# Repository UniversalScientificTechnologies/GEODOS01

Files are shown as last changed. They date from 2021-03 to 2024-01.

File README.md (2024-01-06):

# GEODOS01B - Stand-alone ionizing radiation monitor

*Open-source scintillation detector of ionizing radiation. The device can be further modified according to specific requirements. The character of its construction makes it especially suitable for placement into mountains for in-field measurements*

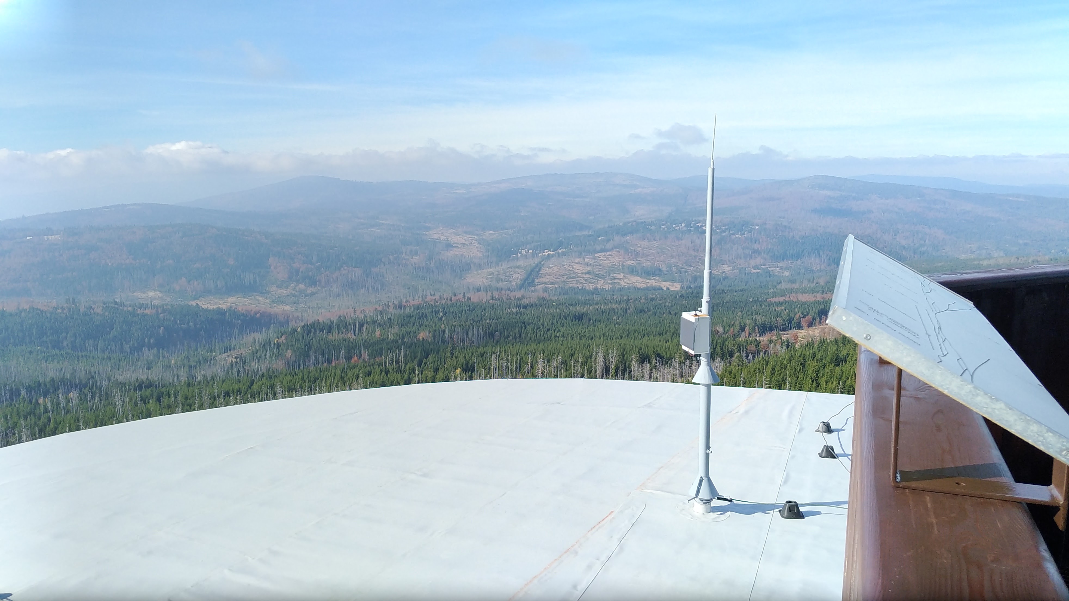
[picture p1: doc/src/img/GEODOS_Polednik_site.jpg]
GEODOS01A Installed on Polednik site


If you need a fully automatic ionizing radiation dosimeter-spectrometer device (with internal logging and a backup power supply) or a device designed for outdoor use without the possibility of connecting to a power supply and data network [GEODOS01](https://github.com/UniversalScientificTechnologies/GEODOS01) might be a better option. We can help you in choosing the most suitable device or even design and develop a new one according to your requirements. In either case, reach us using email [support@ust.cz](mailto:support@ust.cz).

### Locations

GEODOS devices are mounted in multiple significant locations around Europe at this moment.

#### Chernobyl Red Forest

One GEODOS device is installed in [Chernobyl Red Forest site](https://en.wikipedia.org/wiki/Red_Forest).

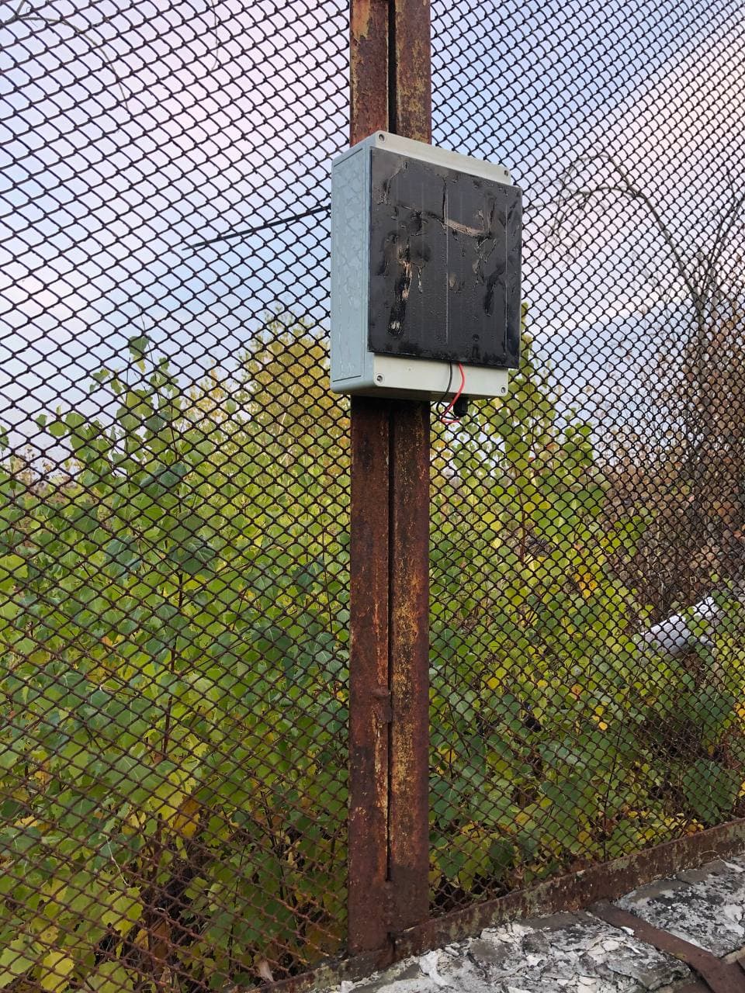
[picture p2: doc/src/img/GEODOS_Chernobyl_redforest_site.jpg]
GEODOS01A Installed in Chernobyl Red Forest site


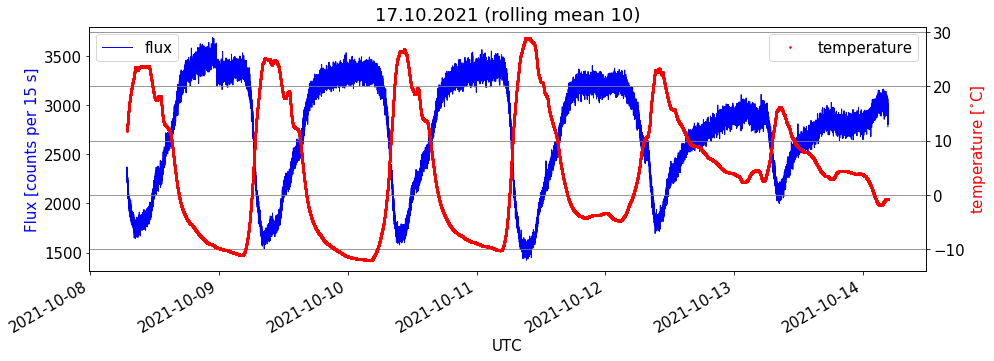
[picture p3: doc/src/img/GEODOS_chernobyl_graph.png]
GEODOS01A raw data before temperature compensation


#### Šumava mountains

GEODOS devices are installed in multiple locations in Šumava. For example example at [Polednik watch tower](https://cs.wikipedia.org/wiki/Poledn%C3%ADk_(%C5%A0umava)).

GEODOS01A Installed on Polednik site

#### Kosetice Atmospheric Tower

The [National Atmospheric Observatory Košetice](https://actris-ri.cz/) (NAOK) was established by the Czech Hydrometeorological Institute as a department specialized in long-term air quality monitoring and research at the background scale in 1988. The GEODOS is located here by [CRREAT project](http://www.ujf.cas.cz/en/research-development/large-research-infrastructures-and-centres/crreat/objectives/).

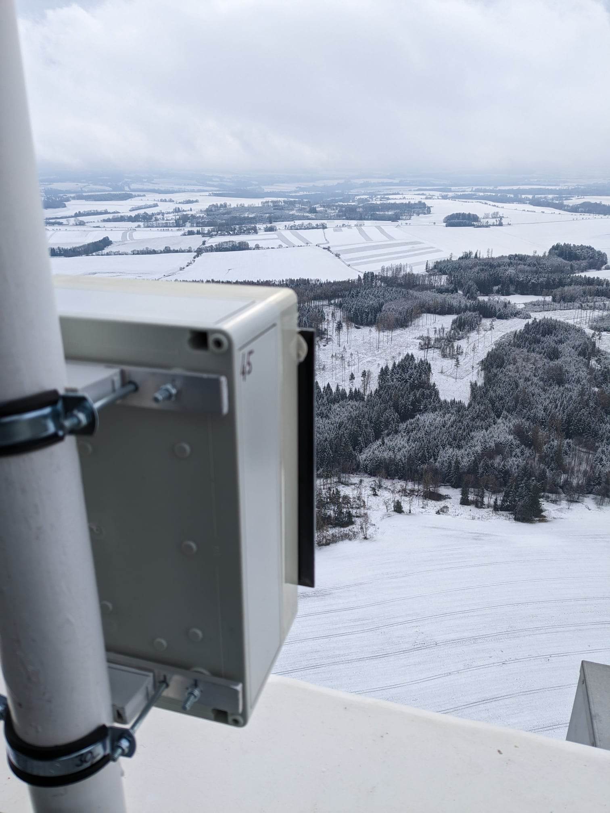
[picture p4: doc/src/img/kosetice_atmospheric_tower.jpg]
GEODOS01B Installed Kosetice Atmospheric Tower


### Technical parameters

* Detection element: scintillation crystal NaI(Tl) 14 mm in diameter, 20 mm in length, integrated with SiPM detector
* Power source: solar panel
* Backup power source: [LTO cells](https://en.wikipedia.org/wiki/Lithium-titanate_battery)
* Data memory: SD card
* Record’s content: energy and time of each event above the specified energy (1MeV by default)
* Record’s periodicity: 10 s (maximal dead time 2 s)
* Time resolution: 20 us
* ADC Conversion time: 104 us
* [Dead time](https://en.wikipedia.org/wiki/Dead_time): 2 us
* Accuracy of event’s time: 500 ns
* Energy range: 0.3 to 18 MeV (deposited energy)
* Spectral Resolution: 0.02 MeV
* Open-source HW and SW
* Device status indicator type: LED
* Uninterrupted measurement campaign interval: 6 months for 2 GB SD card
* LoRa connection to IoT network
* Charging temperature range: -20°C to +35°C
* Operational temperature range: -30°C to +50°C
* Dimensions 254x180x111 mm [enclosure TK PS 2518-11-o](https://www.spelsberg.co.uk/industrial-housing/with-/-without-metric-knock-outs/11090801/)
* Weather protection [IP 33](https://en.wikipedia.org/wiki/IP_code)

### Device block diagram

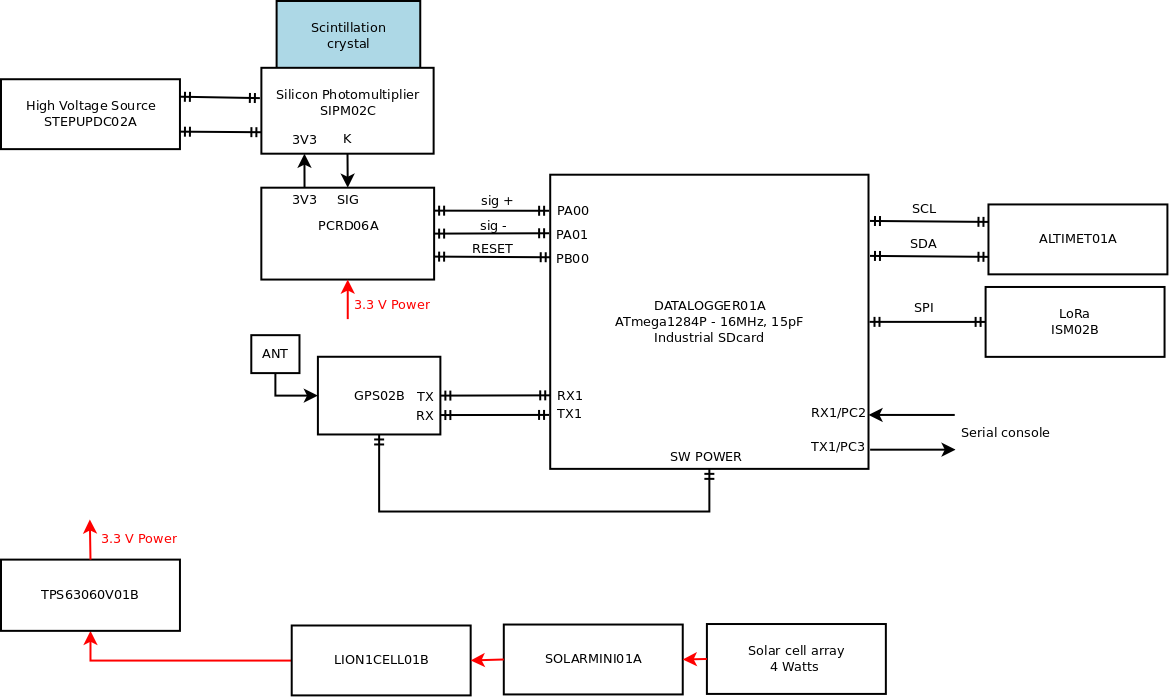
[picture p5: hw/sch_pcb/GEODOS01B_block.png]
GEODOS01A block diagram


### Sensor element

The core of the detector is a scintillation crystal with [SiPM detector](https://en.wikipedia.org/wiki/Silicon_photomultiplier).

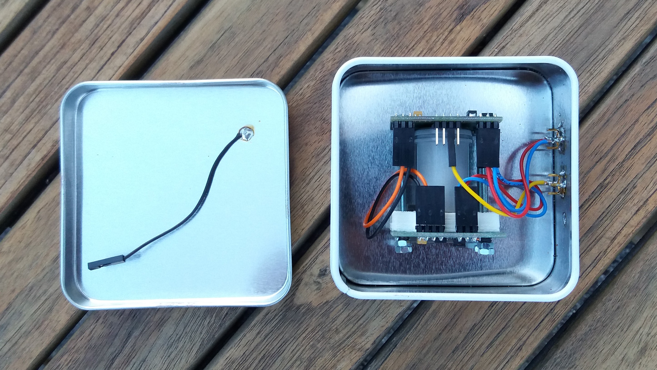
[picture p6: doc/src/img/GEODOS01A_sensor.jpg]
Scintillation detector in box


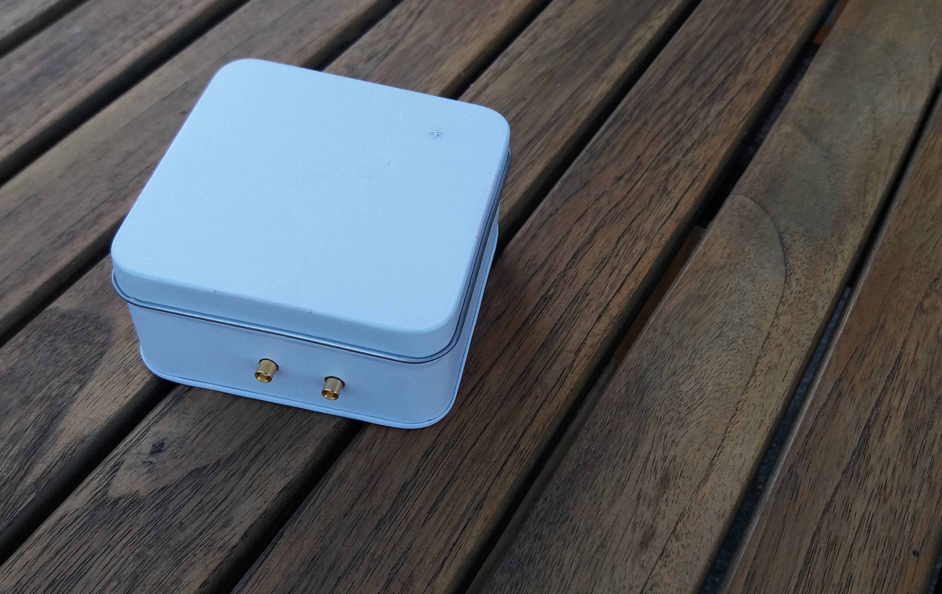
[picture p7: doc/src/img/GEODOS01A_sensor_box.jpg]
Scintillation detector housing


### Data storage

The primary raw data is stored in the SD card's memory. The IoT network is used for telemetry data transfer, and device monitoring (e.g. temperature, humidity, pressure, battery voltage, etc.). We are regularly using the [TTN](https://www.thethingsnetwork.org/), but the device could be configured for use with any IoT LoRa-based network.
For remote areas, mounting an IoT gateway in the radio range of GEODOS instruments could also be a good option.

#### Messages

#### About message

As a second message, when turned on, a string is sent that uniquely identifies the device.

```
$DOS,GEODOS01B,L02,256,379276a,1290c00806a200914056a000a0000086
```
* `$DOS` - is the first character of the message string
* `GEODOS01B` - Name of the device. In this case, it is GEODOS
* `L02`- FW version
* `256` - ADC offset
* `379276a` - Hash of commit with this firmware
* `1290c00806a200914056a000a0000086` - Unique serial number of dosemeter instrument

#### Data message

The output data are in the form of textual [NMEA-0183](https://en.wikipedia.org/wiki/NMEA_0183) like strings. There are two main message types - Histogram message ($HIST) and events stream message ($HITS). Both of these messages could be combined in data output from a single device.  

##### Histogram message

```
$HIST,8,118.15,960.09,4.06,2.33,394,803,0,3,30656,2401,1304,5,3,4,7,9,5,4,6,7,4,3,0,8,2,3,1,1,1,4,3
```

* `$HIST` - Marking a message with spectrums
* `count` - Message number since restart or power-up
* `time` - Time in seconds from power-up
* `suppress` -
* `dose` - Number of detected particles
* `offset` - ADC offset. Specifies the zero channel position.
* `energetic channels` - All remaining values indicate a certain energy channel. From the smallest to the largest. The third value is 1st channel.

##### Events message

```
$HITS,20,916,84,2984,37,16386,38,30666,26,38530,48,43043,27,49257,100,53904,43,59650,32,65631,32,65802,46,68555,47,71124,53,73601,48,74179,59,77454,72,90563,30,98074,74,98901,124,99743,50
```
* `$HITS` - Marking a message with individual events
* `hit count` - Number of events captured from the last HITS message
* `time` - Time in seconds from power-up
* `hit channel` - Channel corresponding to the captured event

### Detailed documentation of the used electronic modules

* [STEPUPDC02A](https://github.com/mlab-modules/STEPUPDC02)
* [SIPM02C](https://github.com/mlab-modules/SIPM02) known as "AIRDOSC01A_PCB01C"
* [PCRD06A](https://github.com/mlab-modules/PCRD06)
* [GPS01B](https://www.mlab.cz/module/GPS01B)
* [DATALOGGER01A](http://mlab.cz/module/DATALOGGER01A)
* [ALTIMET01A](https://github.com/mlab-modules/ALTIMET01)
* [ISM02B](https://github.com/mlab-modules/ISM02)
* [TPS63060V01A](https://github.com/mlab-modules/TPS63060V01)
* [LION1CELL01B](https://github.com/mlab-modules/LION1CELL01)
* [SOLARMINIBAT01A](https://github.com/mlab-modules/SOLARMINIBAT01)
* [SOLARMINI01B](https://github.com/mlab-modules/SOLARMINI01)

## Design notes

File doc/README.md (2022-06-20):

# Advanced user documentation of GEODOS

# Uvedení do provozu

Při instalaci zařízení musí být splněno:

  * Přívod energie - buď fotovoltaickým panelem, nebo napájením z jiného 5V zdroje
  * GPS anténa musí být umístěna tak, aby měla výhled na oblohu (Nalepena na vrchní stranu krabice, do volného okna v observatoři nebo podobně)
  * Do zařízení musí být vložena zformátovaná SDkarta na kterou se budou zapisovat data.  

## Zapnutí přístroje

Po splnění těchto podmínek je možné zařízení zapnout vypínačem. Směrem k LED je zapnuto.

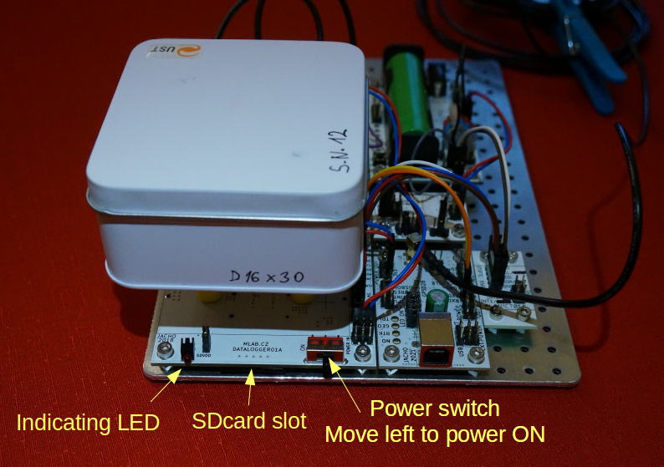
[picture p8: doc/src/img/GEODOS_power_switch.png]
GEODOS01 power switch


Po zapnutí se spustí GPS, což je indikováno LED na modulu GPS02B do kterého vede GPS anténa. Následně zařízení přibližně minutu čeká na získání fixu pozice. Získání fixu je indikováno blikáním zelené LED na modulu GPS02B.
Následně každých 10sekund blikne červená LED na levo od vypínače, což indikuje zápis na SDkartu.

## Získávání dat

GEODOS dovede data na SDkartu zaznamenávat velmi dlouho. Šest měsíců záznamu odpovídá přibližně 500MB dat. Běžné velikosti SDkaret umožňují kontinuální záznam řádově v rocích provozu. Z tohoto důvodu je GEODOS vybaven LoRa telemetrií, aby bylo možno přibližně monitorovat jeho funkčnost.  
Používat GEODOS tímto způsobem ale není úplně rozumné, neboť tato vzdálená telemetrie není schopna monitorovat kvalitu dat. Je tak dobré data manuálně stahovat buď pravidelně, nebo na základě výskytu významných událostí.

## Vypnutí přístroje a vyčtení dat

Díky způsobu fungování, kdy přístroj zaznamenává na SDkartu jednou za 10 sekund je vhodné vypnutí provést tak, že **počkáme na dvojbliknutí červené LED vlevo od vypínače a následně vypínačem vypneme napájení**.
Tento postup minimalizuje možnost poškození souborového systému na SDkartě nedokončeným zápisem.

Následně je možná SDkartu vyjmout zatáhnutím nehtem (SDkarta je umístěna v prostoru mezi vypínačem a indikační LED).

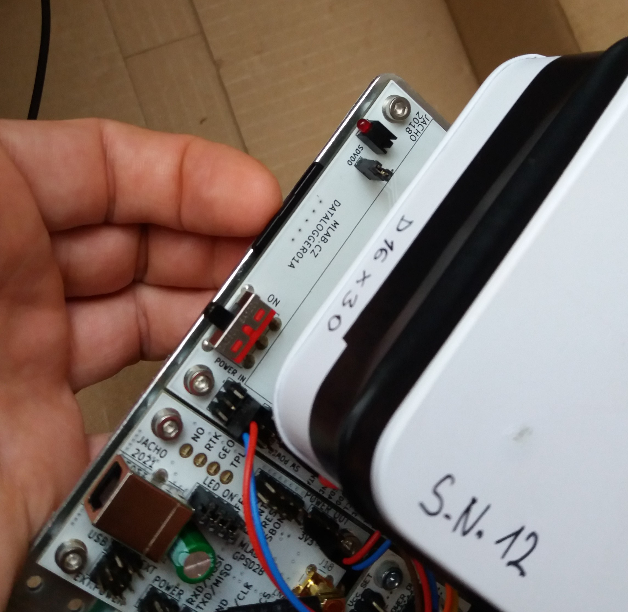
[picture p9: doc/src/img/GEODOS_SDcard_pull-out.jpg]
SDcard removing


SDkartu lze přečíst v běžné čtečce SDkaret. Vyzkoušeným typem je například [Kingston USB 3.0 High-Speed Card Reader](https://www.kingston.com/us/memory-card-readers/usb-3-0-high-speed-media-reader)

Na SDkartě je pak za normílních okolností pouze jeden soubor DATALOG.TXT, který obsahuje všechny zaznamenané informace.  

## Service information

### Debug output

GEODOS has debug output at RX0, TX0 baudrate is 38400.

  $HIST,63,861.90,97386.50,25.81,3.82,16,473,883,2,12704,21600,80,16,11,0,3,5,1,1,3,0,1,2,1,1,1,0,0,1,0,0,0,2
  $HITS,29,4879,35,5201,30,17202,36,18704,30,21061,102,27156,61,27574,79,27797,26,32746,40,40409,58,48144,36,49356,54,51772,37,52090,69,56941,61,62446,36,63116,132,65634,104,67413,35,68563,32,70039,30,70211,56,83196,28,83445,63,87672,32,88476,29,92791,26,99154,84,99543,29

### Firmware upgrade

For the firmware upgrade, the USB-RS232 converter is needed.  Normally is used the [USB232R02](https://github.com/mlab-modules/USB232R02), but any [USBcable](https://techfun.sk/produkt/kabel-pl2303hx-usb-na-ttl-rs232/) could be used.

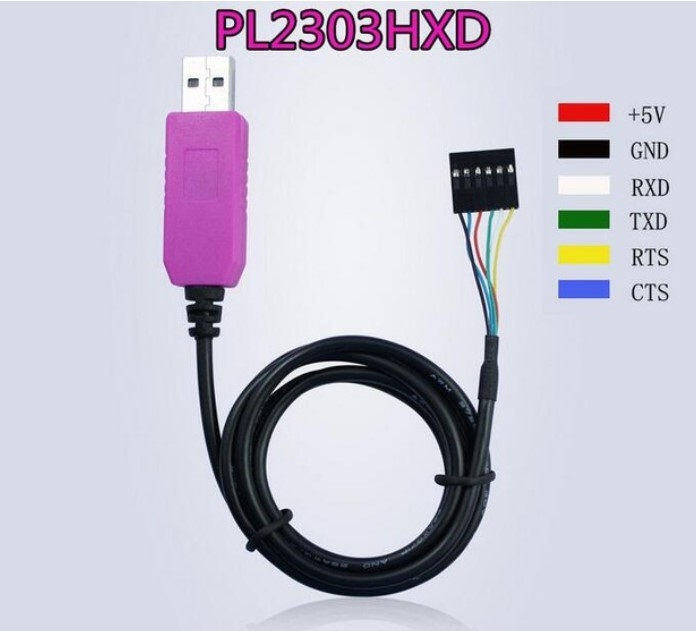
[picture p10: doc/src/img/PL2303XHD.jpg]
PL2303XHD cable


#### Cable connection

|USB converter cable | DATALOGGER01A |
|--------------|---------------|
|RX | TX0|
|TX | RX0|
|RTS | RST# |
|GND | GND|

Physical realization

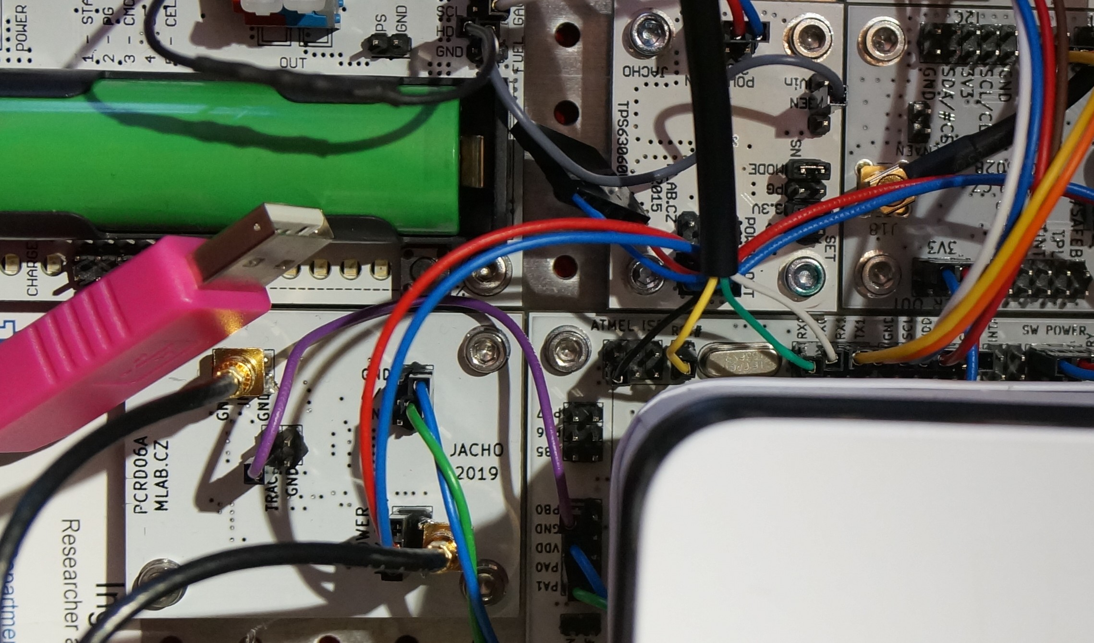
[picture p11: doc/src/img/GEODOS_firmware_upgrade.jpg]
PL2303XHD cable - DATALOGGER01A connection


#### Upgrade process

    cd fw/bin/FIRMWARE_VERSION
    ./program.sh

Expected output:

    $ ./program.sh

    avrdude: Version 6.3-20190619
             Copyright (c) 2000-2005 Brian Dean, http://www.bdmicro.com/
             Copyright (c) 2007-2014 Joerg Wunsch

             System wide configuration file is "./avrdude.conf"
             User configuration file is "/home/kaklik/.avrduderc"
             User configuration file does not exist or is not a regular file, skipping

             Using Port                    : /dev/ttyUSB0
             Using Programmer              : arduino
             Overriding Baud Rate          : 115200
             AVR Part                      : ATmega1284P
             Chip Erase delay              : 55000 us
             PAGEL                         : PD7
             BS2                           : PA0
             RESET disposition             : dedicated
             RETRY pulse                   : SCK
             serial program mode           : yes
             parallel program mode         : yes
             Timeout                       : 200
             StabDelay                     : 100
             CmdexeDelay                   : 25
             SyncLoops                     : 32
             ByteDelay                     : 0
             PollIndex                     : 3
             PollValue                     : 0x53
             Memory Detail                 :

                                      Block Poll               Page                           Polled
               Memory Type Mode Delay Size  Indx Paged  Size   Size #Pages MinW  MaxW       ReadBack
               ----------- ---- ----- ----- ---- ------ ------ ---- ------ ----- ----- --------    -
               eeprom        65    10   128    0 no       4096    8      0  9000  9000 0xff     0xff
               flash         65    10   256    0 yes    131072  256    512  4500  4500 0xff     0xff
               lock           0     0     0    0 no          1    0      0  9000  9000 0x00     0x00
               lfuse          0     0     0    0 no          1    0      0  9000  9000 0x00     0x00
               hfuse          0     0     0    0 no          1    0      0  9000  9000 0x00     0x00
               efuse          0     0     0    0 no          1    0      0  9000  9000 0x00     0x00
               signature      0     0     0    0 no          3    0      0     0     0 0x00     0x00
               calibration    0     0     0    0 no          1    0      0     0     0 0x00     0x00

             Programmer Type : Arduino
             Description     : Arduino
             Hardware Version: 3
             Firmware Version: 8.0
             Vtarget         : 0.3 V
             Varef           : 0.3 V
             Oscillator      : 28.800 kHz
             SCK period      : 3.3 us

    avrdude: AVR device initialized and ready to accept instructions

    Reading | ################################################## | 100% 0.00s

    avrdude: Device signature = 0x1e9705 (probably m1284p)
    avrdude: safemode: lfuse reads as 0
    avrdude: safemode: hfuse reads as 0
    avrdude: safemode: efuse reads as 0
    avrdude: reading input file "./AIRDOSC_1024_LS.ino.hex"
    avrdude: writing flash (25132 bytes):

    Writing | ################################################## | 100% 3.28s

    avrdude: 25132 bytes of flash written
    avrdude: verifying flash memory against ./AIRDOSC_1024_LS.ino.hex:
    avrdude: load data flash data from input file ./AIRDOSC_1024_LS.ino.hex:
    avrdude: input file ./AIRDOSC_1024_LS.ino.hex contains 25132 bytes
    avrdude: reading on-chip flash data:

    Reading | ################################################## | 100% 2.28s

    avrdude: verifying ...
    avrdude: 25132 bytes of flash verified

    avrdude: safemode: lfuse reads as 0
    avrdude: safemode: hfuse reads as 0
    avrdude: safemode: efuse reads as 0
    avrdude: safemode: Fuses OK (E:00, H:00, L:00)

    avrdude done.  Thank you.

The new firmware version should be marked at beginnig of  DATALOG.TXT file after the power-up and logging some data. e.g.

    $AIRDOS,C_LS_1024_v2,...

### Scintillation detector

Scintilační krystaly použité v GEODOSech mají různé rozměry. Rozměr krystalů je napsán na boku bílé kovové krabičky ve které je krystal umístěn.

**Při otevření krabičky je nutné mít vypnuté napájení křemíkového fotonásobiče** Při zapnutém napájení teče na světle skrz SiPM příliš velký proud a fotonásobič se zničí přehřátím.

### Photovoltaic power source

#### Solar cell array parameters

##### Elektrical parameters

- Isc = 2,3 A
- Voc= 2,5 V
- Impp= 2,1 A
- Vmpp= 2,1 V
- Pm= 4,4 Wp

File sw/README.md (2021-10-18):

# Supporting software

`lorasave.py` is a script for general logging of LoRa uplink messages to a file. It works with the The Things Network infrastructure.

It creates log files with newline-separated JSON messages. To process the logged messages and extract specific fields, you may for example use the `jq` tool, like this:

	$ cat __path_to_logs__ | jq -r '[.received_at, .end_device_ids.device_id, .device_id, .uplink_message.decoded_payload.V] | @tsv'

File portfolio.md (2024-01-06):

---
title: "Ground based radiation monitor"
name: "AAA"
excerpt: "Open-source scintillation detector of ionizing radiation. The device can be further modified according to specific requirements. The character of its construction makes it especially suitable for placement into mountains for in-field measurements"
header:
  image: products/GEODOS01B/doc/src/img/kosetice_atmospheric_tower.jpg
  teaser: products/GEODOS01B/doc/src/img/kosetice_atmospheric_tower.jpg
  overlay_color: "#000"
  overlay_filter: "0.5"
  overlay_image: products/GEODOS01B/doc/src/img/GEODOS_Polednik_site.jpg

---

GEODOS01A Installed on Polednik site

If you need a fully automatic ionizing radiation dosimeter-spectrometer device (with internal logging and a backup power supply) or a device designed for outdoor use without the possibility of connecting to a power supply and data network [GEODOS01](https://github.com/UniversalScientificTechnologies/GEODOS01) might be a better option. We can help you in choosing the most suitable device or even design and develop a new one according to your requirements. In either case, reach us using email [support@ust.cz](mailto:support@ust.cz).

### Example installations

GEODOS devices are mounted in multiple significant locations around Europe at this moment.

#### Chernobyl Red Forest

One GEODOS device is installed in [Chernobyl Red Forest site](https://en.wikipedia.org/wiki/Red_Forest).

GEODOS01A Installed in Chernobyl Red Forest site

#### Šumava mountains

GEODOS devices are installed in multiple locations in Šumava. For example example at [Polednik watch tower](https://cs.wikipedia.org/wiki/Poledn%C3%ADk_(%C5%A0umava)).

GEODOS01A Installed on Polednik site

#### Kosetice Atmospheric Tower

The [National Atmospheric Observatory Košetice](https://actris-ri.cz/) (NAOK) was established by the Czech Hydrometeorological Institute as a department specialized in long-term air quality monitoring and research at the background scale in 1988. The GEODOS is located here by [CRREAT project](http://www.ujf.cas.cz/en/research-development/large-research-infrastructures-and-centres/crreat/objectives/).

GEODOS01B Installed Kosetice Atmospheric Tower

### Data storage

The primary raw data is stored in the SD card's memory. The IoT network is used for telemetry data transfer, and device monitoring (e.g. temperature, humidity, pressure, battery voltage, etc.). We are regularly using the [TTN](https://www.thethingsnetwork.org/), but the device could be configured for use with any IoT LoRa-based network.
For remote areas, mounting a private IoT gateway in the radio range of GEODOS instruments could also be an option.

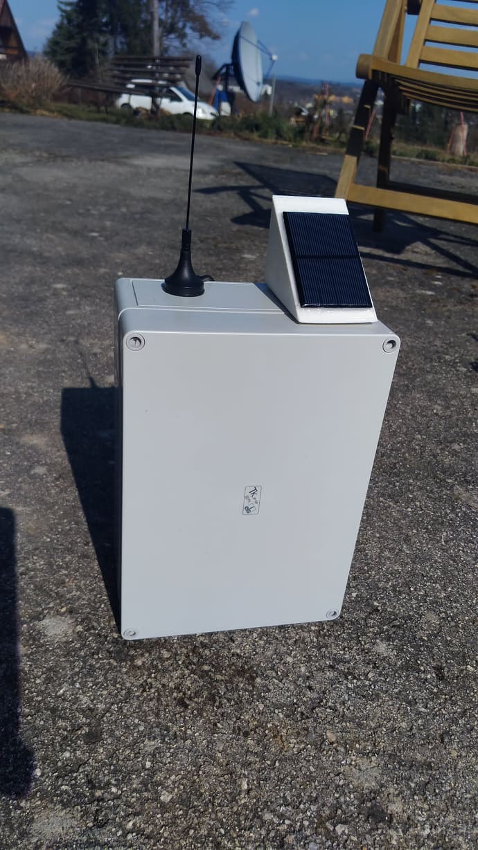
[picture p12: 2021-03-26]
doc/src/img/GEODOS01A.jpg

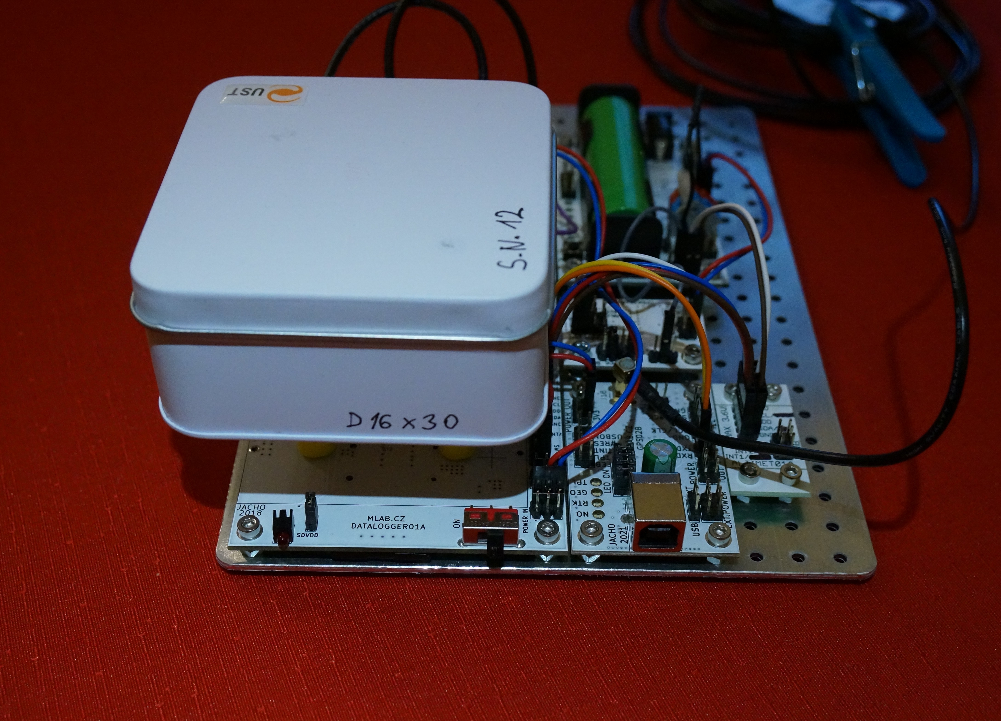
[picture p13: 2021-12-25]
doc/src/img/GEODOS_power_switch.jpg

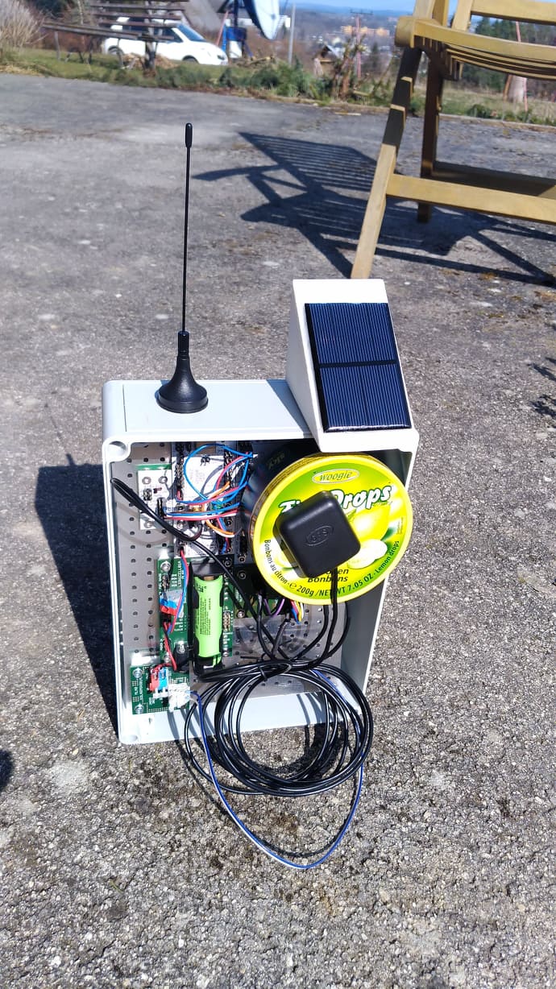
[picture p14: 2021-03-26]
doc/src/img/GEODOS01A_opened.jpg

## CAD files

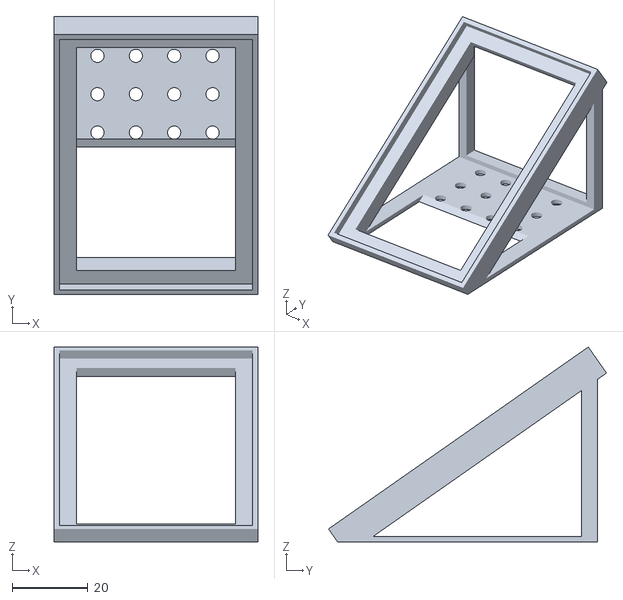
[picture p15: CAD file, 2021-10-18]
cad/stl/SolarHolder.stl
54.0 x 73.6 x 51.6

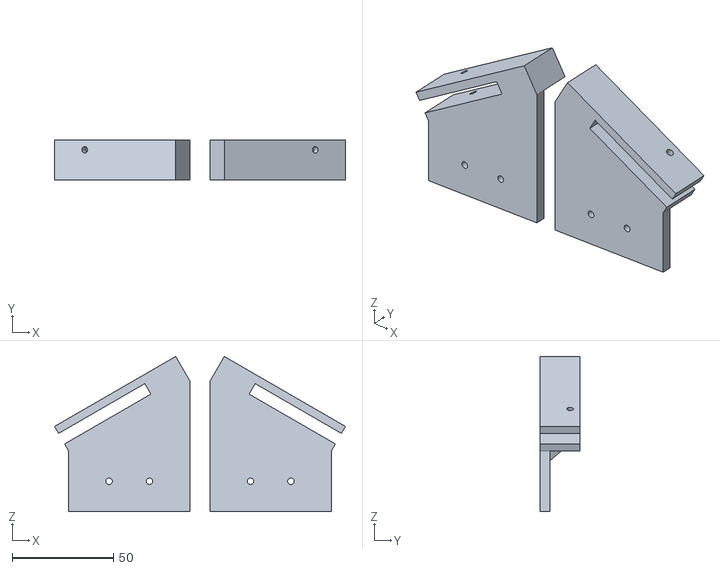
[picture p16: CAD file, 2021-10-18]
cad/stl/SolarHolder_big.stl
144.0 x 20.0 x 76.8

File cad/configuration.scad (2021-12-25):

$fn=40; // model faces resolution.

//OBECNE PARAMETRY 
//----------------------------------------------------------------
//----------------------------------------------------------------

vyska_krystalu=15;
vyska_sipm=2;
presah_krystalu=6;
rezerva_nad_krystalem=5;
vyska_drzaku_krystalu=vyska_krystalu-presah_krystalu-2;

hrana_krystalu=6; //čistá hrana

// big-big
//zakladna_krystalu_x=23.7; //1.5mm rezerva hrana SIPM je 22 mm
//zakladna_krystalu_y=23.7;
// big-small
zakladna_krystalu_x=22.0; //1.5mm rezerva hrana SIPM je 22 mm
zakladna_krystalu_y=22.0;
sila_steny=1.2;
sila_materialu_zakladny=7; //1.6;


vyska_zapusti_pro_PCB=0; //výčka krycího matriálu pro PCB a zároveň pro vytvoření vany pro zalití silikonem, kvůli světlotěsnoti.
vyska_SIPM_nad_PCB=2.4; //výška celého SIPM senzoru
tolerance_pro_dotazeni_k_SIPM=-0.5; // kvůli dotažení krystalu k SIPM
velikost_modulu_x=2; //počet der
velikost_modulu_y=4;
rotec_der_modulu=10.16;

vyska_matky=3;
sirka_matky=6.7;
prumer_sroubu=3.6;//3.4;
prumer_hlavy_sroubu=6;
vyska_hlavy_sroubu=5;

//Pro díl SIPMBOX01C_D02
D02_velikost_modulu_x=3; //počet der
D02_velikost_modulu_y=4;
D02_vyska_bocniho_prekryvu=25;

//Pro díl SIPMBOX01C_D07
D07_vyska=6;

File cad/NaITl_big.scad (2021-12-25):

include <./configuration.scad>
 
/*
difference (){
SIPMBOX01C_D05();
 
translate([-(hrana_krystalu)/2,-(hrana_krystalu)/2,0])
         
   cube([100,100,100]);   
    
}
*/

/*
difference (){
      union() {
translate([0,0,7])
          
          translate([-rotec_der_modulu/2,0,0])
          SIPMBOX01C_D01();
          
         
SIPMBOX01C_D02();

translate([-rotec_der_modulu/2,0,0])
SIPMBOX01C_D06();


SIPMBOX01C_D07();
 
 
translate([-10/2,-(D02_velikost_modulu_y+2)*rotec_der_modulu/2,sila_materialu_zakladny+vyska_krystalu+rezerva_nad_krystalem])          
SIPMBOX01C_D08();          
          

translate([-rotec_der_modulu/2,0,0])
SIPMBOX01C_D03();

translate([-(hrana_krystalu)/2,-(hrana_krystalu)/2,0])
cube([hrana_krystalu,hrana_krystalu,vyska_krystalu+vyska_sipm]);
          }
   cube([100,100,100]);       
          
          }

//*/



 SIPMBOX01C_D01();

//SIPMBOX01C_D06();

//SIPMBOX01C_D02();


 

module SIPMBOX01C_D08()
{
  vyska_sloupku=3;
   difference () 
    {
   union()       {   
    cube([10,(D02_velikost_modulu_y+2)*rotec_der_modulu,2],center=false); 
        translate([10/2,0,0]) 
        cylinder (h = 3, r= 10/2, $fn=20);
        
     translate([10/2,(D02_velikost_modulu_y+2)*rotec_der_modulu,0]) 
        cylinder (h = 3, r= 10/2, $fn=20);
    }
    
     translate([10/2,0,-0.01]) 
            cylinder (h = vyska_sloupku+1, r= (prumer_sroubu+0.2)/2, $fn=40);
    
     translate([10/2,(D02_velikost_modulu_y+2)*rotec_der_modulu,-0.01]) 
            cylinder (h = vyska_sloupku+1, r= (prumer_sroubu+0.2)/2, $fn=40);
    
    
    }
    
    
       
}





module SIPMBOX01C_D07() //drzak na ALBASE
{
  difference (){
      union() {
 //Zakladna
 translate([-((D02_velikost_modulu_x) * rotec_der_modulu+2*sila_materialu_zakladny)/2,-((D02_velikost_modulu_y+2) * rotec_der_modulu+2*sila_materialu_zakladny)/2,0])
 
 minkowski()
{
  cube([(D02_velikost_modulu_x) * rotec_der_modulu+2*sila_materialu_zakladny,(D02_velikost_modulu_y+2) * rotec_der_modulu+2*sila_materialu_zakladny,D07_vyska]);
  cylinder(r=2,h=0.1);
}







}

//otvor na cely scintilacni detektor 
translate([-(D02_velikost_modulu_x * rotec_der_modulu+2*sila_materialu_zakladny)/2+2-1,-(D02_velikost_modulu_y * rotec_der_modulu+2*sila_materialu_zakladny)/2+2-1,0])
 
 minkowski()
{
  cube([D02_velikost_modulu_x * rotec_der_modulu-2*2+2+2*sila_materialu_zakladny,D02_velikost_modulu_y * rotec_der_modulu-2*2+2+2*sila_materialu_zakladny,D07_vyska]);
  cylinder(r=2,h=0.1);
}


//otvor na sroub 1
translate([-(D02_velikost_modulu_x-1)*rotec_der_modulu/2,(D02_velikost_modulu_y+2)*rotec_der_modulu/2,-0.01]) 
    translate([0,0,-0.01]) 
        {
        cylinder (h = D07_vyska+0.12, r= (prumer_sroubu+0.2)/2, $fn=40);
    
        cylinder (h = vyska_matky, r= (sirka_matky+0.2)/2, $fn=6);
      
        }

//otvor na sroub 2
translate([(D02_velikost_modulu_x-1)*rotec_der_modulu/2,(D02_velikost_modulu_y+2)*rotec_der_modulu/2,-0.01]) 
    translate([0,0,-0.01]) 
        {
        cylinder (h = D07_vyska+0.12, r= (prumer_sroubu+0.2)/2, $fn=40);
    
        cylinder (h = vyska_matky, r= (sirka_matky+0.2)/2, $fn=6);
      
        }

//otvor na sroub 3
translate([-(D02_velikost_modulu_x-1)*rotec_der_modulu/2,-(D02_velikost_modulu_y+2)*rotec_der_modulu/2,-0.01]) 
    translate([0,0,-0.01]) 
        {
        cylinder (h = D07_vyska+0.12, r= (prumer_sroubu+0.2)/2, $fn=40);
    
        cylinder (h = vyska_matky, r= (sirka_matky+0.2)/2, $fn=6);
      
        }

//otvor na sroub 4
translate([(D02_velikost_modulu_x-1)*rotec_der_modulu/2,-(D02_velikost_modulu_y+2)*rotec_der_modulu/2,-0.01]) 
    translate([0,0,-0.01]) 
        {
        cylinder (h = D07_vyska+0.12, r= (prumer_sroubu+0.2)/2, $fn=40);
    
        cylinder (h = vyska_matky, r= (sirka_matky+0.2)/2, $fn=6);
      
        }
 
//Otvor na uchytny sroub 1
translate([0,(D02_velikost_modulu_y+2)*rotec_der_modulu/2,0]) 
    translate([0,0,-0.01]) 
        {
        cylinder (h = D07_vyska+0.12, r= (prumer_sroubu+0.2)/2, $fn=40);
         cylinder (h = vyska_hlavy_sroubu, r= (prumer_hlavy_sroubu+0.2)/2, $fn=40);
                      
        }

//Otvor na uchytny sroub 2
translate([0,-(D02_velikost_modulu_y+2)*rotec_der_modulu/2,-0.01]) 
    translate([0,0,-0.01]) 
        {
        cylinder (h = D07_vyska+0.12, r= (prumer_sroubu+0.2)/2, $fn=40);
   cylinder (h = vyska_hlavy_sroubu, r= (prumer_hlavy_sroubu+0.2)/2, $fn=40);
        }      
        
 
} 
}           
         

module SIPMBOX01C_D05() //drzak krystalu
{
  difference (){
      union() {
 //Zakladna
 translate([-(velikost_modulu_x * rotec_der_modulu)/2+2+1/2,-(velikost_modulu_y * rotec_der_modulu)/2+2+1/2,0])
 
 minkowski()
{
  cube([velikost_modulu_x * rotec_der_modulu-2*2-1,velikost_modulu_y * rotec_der_modulu-2*2-1,sila_materialu_zakladny]);
  cylinder(r=2,h=0.1);
}


//drzak krystalu
 translate([-(zakladna_krystalu_x+4*sila_steny)/2+2,-(zakladna_krystalu_y+4*sila_steny)/2+2,0])
 
 minkowski()
{
  cube([zakladna_krystalu_x-2*2+4*sila_steny,zakladna_krystalu_y-2*2+4*sila_steny,vyska_drzaku_krystalu+1.5]);
  cylinder(r=2,h=0.1);
}
}

//otvor pro dilec 01D
 translate([-(zakladna_krystalu_x+2*sila_steny+1.5)/2+2,-(zakladna_krystalu_y+2*sila_steny+1.5)/2+2,0])
 
 minkowski()
{
  cube([zakladna_krystalu_x-2*2+2*sila_steny+1.5,zakladna_krystalu_y-2*2+2*sila_steny+1.5,vyska_drzaku_krystalu]);
  cylinder(r=2,h=0.1);
}


//otvor na sroub 1
translate([(velikost_modulu_x-1)*rotec_der_modulu/2,(velikost_modulu_y-1)*rotec_der_modulu/2,-0.01]) 
 
 translate([0,0,-0.01]) 
        cylinder (h = sila_materialu_zakladny+0.12, r= (prumer_sroubu+0.2)/2, $fn=40);


 //otvor na sroub 2
    translate([-(velikost_modulu_x-1)*rotec_der_modulu/2,(velikost_modulu_y-1)*rotec_der_modulu/2,-0.01]) 
      translate([0,0,-0.01]) 
        cylinder (h = sila_materialu_zakladny+0.12, r= (prumer_sroubu+0.2)/2, $fn=40);

    //otvor na sroub 3
    translate([(velikost_modulu_x-1)*rotec_der_modulu/2,-(velikost_modulu_y-1)*rotec_der_modulu/2,-0.01]) 
      translate([0,0,-0.01]) 
        cylinder (h = sila_materialu_zakladny+0.12, r= (prumer_sroubu+0.2)/2, $fn=40);
//otvor na sroub 4
    translate([-(velikost_modulu_x-1)*rotec_der_modulu/2,-(velikost_modulu_y-1)*rotec_der_modulu/2,-0.01]) 
      translate([0,0,-0.01]) 
        cylinder (h = sila_materialu_zakladny+0.12, r= (prumer_sroubu+0.2)/2, $fn=40);
 
 
 //otvor na krystal
 
 translate([-(zakladna_krystalu_x)/2,-(zakladna_krystalu_y)/2,0])
 cube([zakladna_krystalu_x,zakladna_krystalu_y,vyska_drzaku_krystalu+0.12]);
} 
} 



module SIPMBOX01C_D03() //vrchní kryt
{
  difference (){
      union() {
 //Zakladna
 translate([-(velikost_modulu_x * rotec_der_modulu+2*sila_materialu_zakladny)/2+2,-(velikost_modulu_y * rotec_der_modulu+2*sila_materialu_zakladny)/2+2,0])
 
 minkowski()
{
  cube([velikost_modulu_x * rotec_der_modulu-2*2+2*sila_materialu_zakladny,velikost_modulu_y * rotec_der_modulu-2*2+2*sila_materialu_zakladny,sila_materialu_zakladny+vyska_krystalu+rezerva_nad_krystalem]);
  cylinder(r=2,h=0.1);
}


}

//odstranění vnitřního prostoru ve tvaru krychle
 translate([-(velikost_modulu_x * rotec_der_modulu)/2,-(velikost_modulu_y * rotec_der_modulu)/2,sila_materialu_zakladny])
cube([velikost_modulu_x * rotec_der_modulu,velikost_modulu_y * rotec_der_modulu,sila_materialu_zakladny+vyska_krystalu+rezerva_nad_krystalem]);


 
} 
} 

module SIPMBOX01C_D02() //kryt ze spoda
{
  difference (){
      union() {
 //Zakladna
 translate([-(D02_velikost_modulu_x * rotec_der_modulu+2*sila_materialu_zakladny)/2+2,-(D02_velikost_modulu_y * rotec_der_modulu+2*sila_materialu_zakladny)/2+2,0])
 
 minkowski()
{
  cube([D02_velikost_modulu_x * rotec_der_modulu-2*2+2*sila_materialu_zakladny,D02_velikost_modulu_y * rotec_der_modulu-2*2+2*sila_materialu_zakladny,sila_materialu_zakladny+D02_vyska_bocniho_prekryvu]);
  cylinder(r=2,h=0.1);
}



}

 translate([-(D02_velikost_modulu_x * rotec_der_modulu)/2-1/2,-(D02_velikost_modulu_y * rotec_der_modulu)/2-1/2,sila_materialu_zakladny/3*2])
#cube([D02_velikost_modulu_x * rotec_der_modulu+1,D02_velikost_modulu_y * rotec_der_modulu+1,sila_materialu_zakladny+D02_vyska_bocniho_prekryvu]);
for(i=[0:2:12]) 
  translate([0,i-12/2,sila_materialu_zakladny+D02_vyska_bocniho_prekryvu]) rotate([90,0,90]) cylinder(r=0.7,h=20);

} 
} 
 
 module SIPMBOX01C_D01() //drzak krystalu
{
  difference (){
      union() {
 //Zakladna
 translate([-(velikost_modulu_x * rotec_der_modulu)/2+2+1/2,-(velikost_modulu_y * rotec_der_modulu)/2+2+1/2,0])
 
 minkowski()
{
  cube([velikost_modulu_x * rotec_der_modulu-2*2-1,velikost_modulu_y * rotec_der_modulu-2*2-1,sila_materialu_zakladny]);
  cylinder(r=2,h=0.1);
}
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

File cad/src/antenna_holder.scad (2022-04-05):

//use<Write.scad>
$fn=100;

x_size = 20;           // horizontal outer size of the pedestal. 
y_size = 20;           // 
nut_size = 6.8;
SMA_dia = 7.0;
SMA_flat = 3.15;
thickness = 6;         //
wall_thickness = 2;
height = 55;

mount_hole = 3.7;
clear = 0.175;

MLAB_grid = 10.16;

x_holes = floor(x_size / MLAB_grid);
y_holes = floor(y_size / MLAB_grid);

MLAB_grid_xoffset = (x_size - (x_holes * MLAB_grid))/2;
MLAB_grid_yoffset = (y_size - (y_holes * MLAB_grid))/2;

//Top part

union () {

    difference () {
                cube([x_size, y_size , thickness ]);

// MLAB grid holes
        grid_list = [for (j = [MLAB_grid_xoffset : MLAB_grid: x_size], i = [MLAB_grid_yoffset :MLAB_grid: y_size])  [j, i] ];
            
        for (j = grid_list) {
                translate (concat(j, [0]))
                    cylinder (h = 3, r= nut_size/2, $fn=6);
                translate (concat(j, [3.2]))  // one solid layer for slicer (the holes will be pierced on demand )
                    cylinder (h = thickness, r= mount_hole/2, $fn=30);
                //translate (concat(j, [6.0]))
                //    cylinder (h = 10, r= nut_size/2, $fn=6);
        }  
    };
// vertical to horizontal brick connection
    translate ([ 0, 0, thickness - sqrt(2 * wall_thickness*wall_thickness) / 2])  // move to correct positon on square diagonal  
        rotate([45,0,0])
            cube([x_size, wall_thickness , wall_thickness ]);
// rib
    difference()
    {
        translate ([ (x_size / 2) - wall_thickness / 2, 0, -y_size ])  // move to correct positon on square diagonal  
            rotate([45,0,0])
                cube([wall_thickness, y_size*1.4, y_size*1.4]);
        translate ([ 0, -y_size , -thickness * 4]) cube([2*x_size, 2*y_size , thickness * 4 ]);
        translate ([ 0, -y_size - wall_thickness, 0]) cube([x_size, y_size , thickness * 3 ]);
    };
    
    difference  () {

        translate ([0, -wall_thickness, 0])    // vertical brick
            cube([y_size, wall_thickness , height ]);
        
// SMA connector hole
        translate ([ x_size/2, wall_thickness/2, 1.5*(height - thickness)/3  + thickness - SMA_dia/2])    
            rotate([90,0,0]) {
                difference  () {
                    cylinder (h = 2*wall_thickness, r= SMA_dia/2, $fn=50);
                        translate([ 0, SMA_flat , wall_thickness/2 + wall_thickness ]) 
                            cube([SMA_dia, 1 , thickness ], center=true);
                }
            }

        translate ([ x_size/2, wall_thickness/2, 2.3*(height - thickness)/3  + thickness  + SMA_dia/2 ])    
            rotate([90,0,0]){
                difference  () {
                    cylinder (h = 2*wall_thickness, r= SMA_dia/2, $fn=50);
                        translate([ 0, SMA_flat , wall_thickness/2 + wall_thickness ]) 
                            cube([SMA_dia, 1 , thickness ], center=true);
                }
 
           }
           
    }
               
           
}

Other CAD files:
cad/src/BoxHolder.scad
cad/SolarHolder_big.amf
cad/src/SolarHolder.scad
cad/src/SolarHolder_big.scad
cad/src/SpacedosHolder.scad

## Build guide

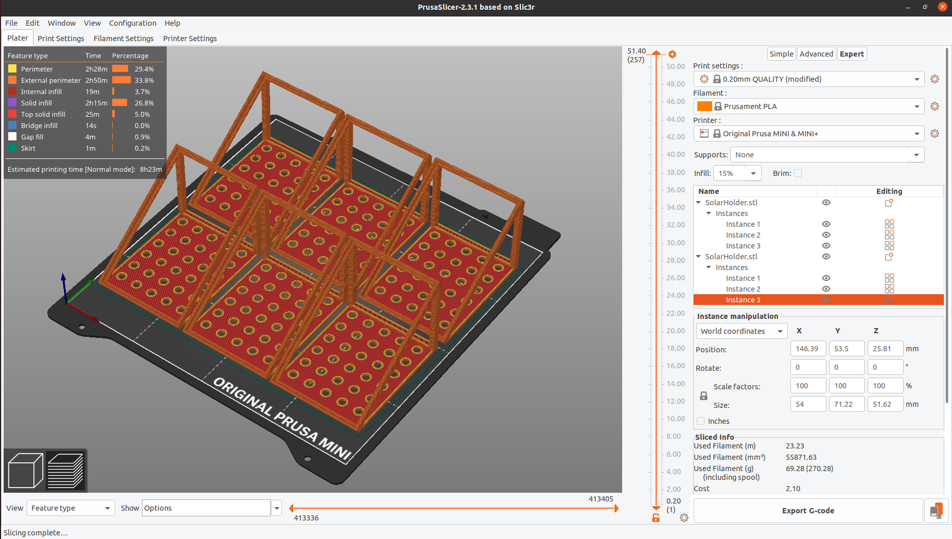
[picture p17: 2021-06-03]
doc/src/img/holder_print_setup.png

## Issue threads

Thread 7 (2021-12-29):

### ISSUE TITLE
Vyřešení potíží s novou verzí obvodu BQ34Z100

### ISSUE THREAD

**Issue by kaklik** [UniversalScientificTechnologies/GEODOS01#7]
Nově vyrobené moduly LION1CELL01jsou osazeny novou verzí obvodu [BQ34Z100](https://www.ti.com/product/BQ34Z100) označovanou jako [BQ34Z100-G1](https://www.ti.com/product/BQ34Z100-G1). 

Oba čipy se  vzájemně liší [zřejmě hlavně firmwarem](https://e2e.ti.com/support/power-management/f/power-management-forum/653763/bq34z100-g1-bq34z100-to-bq34z100-g1-change-list).  Zřejmě existuje možnost do nového čipu nahrát starý firmware. Dělá se to [pravděpodobně přes I2C](https://e2e.ti.com/support/power-management/f/power-management-forum/464735/bq34z100-g-in-system-flash-programming-help).

**Comment by kaklik** [comment]
Existuje několik knihoven pro Arduino, které by měly umět zacházet s oběma typy obvodů: 

- https://github.com/xkam1x/BQ34Z100G1
- https://github.com/tony-cloud/BQ34Z100
- https://github.com/Ralim/BQ34Z100

**Comment by kakl** [comment]
FW pocita s novou verzi BQ34Z100-G1
nastaveni nove verze se dela pres FW pro datalogger

**Comment by kaklik** [comment]
Obvod se nastavuje [tímto firmwarem](https://github.com/ODZ-UJF-AV-CR/GEODOS01/blob/GEODOS01A/fw/guage_setup/guage_setup.ino).

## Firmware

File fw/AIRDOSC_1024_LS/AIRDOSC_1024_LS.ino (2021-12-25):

// R = 12 k OHM
// 0.015 * CH + 0.268 [MeV]
// CH0 = 14
// 1024 ch. from 0.27 to cca 15 MeV

#define DEBUG // Please comment it if you are not debugging
String gittag = "0";
String FWversion = "C_LS_1024"; // Output data format

#define RANGE 25  // histogram range
#define EVENTS 500 // maximal number of recorded events
#define CHANNELS 512    // number of channels in buffer for histogram, including negative numbers
#define GPSerror 700000 // number of cycles for waitig for GPS in case of GPS error 
//#define GPSdelay  3   // number of measurements between obtaining GPS position
//#define GPSdelay  60   // number of measurements between obtaining GPS position cca 10 minutes
#define GPSdelay 2700   // number of measurements between obtaining GPS position and time
                        // 2700 = cca 12.5 h
#define GPSWAIT 600 // more than 50 s waiting for GPS fix
//#define GPSWAIT 60 // less waiting for GPS fix

// Compiled with: Arduino 1.8.13

/*
  AORDOS_C for GeoDos

ISP
---
PD0     RX
PD1     TX
RESET#  through 50M capacitor to RST#

SDcard
------
DAT3   SS   4 B4
CMD    MOSI 5 B5
DAT0   MISO 6 B6
CLK    SCK  7 B7

ANALOG
------
+      A0  PA0
-      A1  PA1
RESET  0   PB0

LED
---
LED_red  23  PC7         // LED for Dasa

LoRa Modem
----------
SX1262_RESET, 21, PC5
SX1262_BUSY, 18, PC2
SX1262_DIO1, 19, PC3
CS, 20, PC4
MOSI, 5, PB5
MISO, 6, PB6
SCK, 7, PB7

SD Card Power
-------------
SDpower1  1    // PB1
SDpower2  2    // PB2
SDpower3  3    // PB3

GPS Power
---------
GPSpower  26   // PA2



                     Mighty 1284p    
                      +---\/---+
           (D 0) PB0 1|        |40 PA0 (AI 0 / D24)
           (D 1) PB1 2|        |39 PA1 (AI 1 / D25)
      INT2 (D 2) PB2 3|        |38 PA2 (AI 2 / D26)
       PWM (D 3) PB3 4|        |37 PA3 (AI 3 / D27)
    PWM/SS (D 4) PB4 5|        |36 PA4 (AI 4 / D28)
      MOSI (D 5) PB5 6|        |35 PA5 (AI 5 / D29)
  PWM/MISO (D 6) PB6 7|        |34 PA6 (AI 6 / D30)
   PWM/SCK (D 7) PB7 8|        |33 PA7 (AI 7 / D31)
                 RST 9|        |32 AREF
                VCC 10|        |31 GND
                GND 11|        |30 AVCC
              XTAL2 12|        |29 PC7 (D 23)
              XTAL1 13|        |28 PC6 (D 22)
      RX0 (D 8) PD0 14|        |27 PC5 (D 21) TDI
      TX0 (D 9) PD1 15|        |26 PC4 (D 20) TDO
RX1/INT0 (D 10) PD2 16|        |25 PC3 (D 19) TMS
TX1/INT1 (D 11) PD3 17|        |24 PC2 (D 18) TCK
     PWM (D 12) PD4 18|        |23 PC1 (D 17) SDA
     PWM (D 13) PD5 19|        |22 PC0 (D 16) SCL
     PWM (D 14) PD6 20|        |21 PD7 (D 15) PWM
                      +--------+
*/

#include <SD.h>             // Revised version from MightyCore
#include "wiring_private.h"
#include <Wire.h>           
#include <Adafruit_MPL3115A2.h>
//#include <avr/wdt.h>

//#include <stdio.h>
//#include <stdint.h>

#include <SPI.h>

#define LED_red   23   // PC7
#define RESET     0    // PB0
#define GPSpower  26   // PA2
#define SDpower1  1    // PB1
#define SDpower2  2    // PB2
#define SDpower3  3    // PB3
#define SS        4    // PB4
#define MOSI      5    // PB5
#define MISO      6    // PB6
#define SCK       7    // PB7
#define INT       20   // PC4
#define IOT_RESET 21   // PC5
#define IOT_BUSY  18   // PC2
#define IOT_DIO1  19   // PC3
#define IOT_CS    20   // PC4

uint16_t count = 0;
uint32_t serialhash = 0;
uint8_t lo, hi;
uint16_t u_sensor, maximum;
Adafruit_MPL3115A2 sensor = Adafruit_MPL3115A2();
uint32_t last_packet = 0;
uint16_t hits;

// Read Analog Differential without gain (read datashet of ATMega1280 and ATMega2560 for refference)
// Use analogReadDiff(NUM)
//   NUM  | POS PIN             | NEG PIN           |   GAIN
//  0 | A0      | A1      | 1x
//  1 | A1      | A1      | 1x
//  2 | A2      | A1      | 1x
//  3 | A3      | A1      | 1x
//  4 | A4      | A1      | 1x
//  5 | A5      | A1      | 1x
//  6 | A6      | A1      | 1x
//  7 | A7      | A1      | 1x
//  8 | A8      | A9      | 1x
//  9 | A9      | A9      | 1x
//  10  | A10     | A9      | 1x
//  11  | A11     | A9      | 1x
//  12  | A12     | A9      | 1x
//  13  | A13     | A9      | 1x
//  14  | A14     | A9      | 1x
//  15  | A15     | A9      | 1x
#define PIN 0
uint8_t analog_reference = INTERNAL2V56; // DEFAULT, INTERNAL, INTERNAL1V1, INTERNAL2V56, or EXTERNAL

uint8_t bcdToDec(uint8_t b)
{
  return ( ((b >> 4)*10) + (b%16) );
}


uint32_t tm;
uint8_t tm_s100;

void readRTC()
{
  Wire.beginTransmission(0x51);
  Wire.write(0);
  Wire.endTransmission();
  
  Wire.requestFrom(0x51, 6);
  tm_s100 = bcdToDec(Wire.read());
  uint8_t tm_sec = bcdToDec(Wire.read() & 0x7f);
  uint8_t tm_min = bcdToDec(Wire.read() & 0x7f);
  tm = bcdToDec(Wire.read());
  tm += bcdToDec(Wire.read()) * 100;
  tm += bcdToDec(Wire.read()) * 10000;
  tm = tm * 60 * 60 + tm_min * 60 + tm_sec;
}

#define BQ34Z100 0x55

int16_t readBat(int8_t regaddr)
{
  Wire.beginTransmission(BQ34Z100);
  Wire.write(regaddr);
  Wire.endTransmission();
  
  Wire.requestFrom(BQ34Z100,1);
  
  unsigned int low = Wire.read();
  
  Wire.beginTransmission(BQ34Z100);
  Wire.write(regaddr+1);
  Wire.endTransmission();
  
  Wire.requestFrom(BQ34Z100,1);
  
  unsigned int high = Wire.read();
  
  unsigned int high1 = high<<8;
  
  return (high1 + low);
}

#define SD_ON     1
#define SD_OFF    2
#define GPS_ON    3
#define GPS_OFF   4
#define LORA_ON   5
#define LORA_OFF  6


void set_power(uint8_t state)
{
  switch(state)
  {
    case SD_ON:
      pinMode(MISO, OUTPUT);     
      pinMode(MOSI, OUTPUT);     
      PORTB |= 0b00001110;
      digitalWrite(SS, LOW);  
      break;
    case SD_OFF:
      digitalWrite(SS, HIGH);  
      PORTB &= 0b11110001;
      break;
    case GPS_ON:
      digitalWrite(GPSpower, HIGH);  
      break;      
    case GPS_OFF:
      digitalWrite(GPSpower, LOW);  
      break;
    case LORA_ON:
      digitalWrite(IOT_CS, LOW);  
      break;
    case LORA_OFF:
      digitalWrite(IOT_CS, HIGH);  
      break;
    default:
      delay(100);
  }
}
  
void setup()
{
  pinMode(SDpower1, OUTPUT);  // SDcard interface
  pinMode(SDpower2, OUTPUT);     
  pinMode(SDpower3, OUTPUT);     
  pinMode(GPSpower, OUTPUT);  // GPS Power    
  pinMode(IOT_CS, OUTPUT);     
  pinMode(SS, OUTPUT);     
  pinMode(MOSI, OUTPUT);     
  pinMode(MISO, OUTPUT);     
  pinMode(SCK, OUTPUT);  
  pinMode(RESET, OUTPUT);   // reset signal for peak detetor

  set_power(SD_OFF);
  set_power(GPS_OFF);
  set_power(LORA_OFF);
  
  //watchdog enable
  //!!!wdt_enable(WDTO_8S);

  Wire.setClock(100000);

  // Open serial communications
  Serial.begin(38400);
  Serial1.begin(38400);

  Serial.println("#Cvak...");
 
  ADMUX = (analog_reference << 6) | ((PIN | 0x10) & 0x1F);
  
  //ADCSRB = 0;               // Switching ADC to Free Running mode
  //sbi(ADCSRA, ADATE);       // ADC autotrigger enable (mandatory for free running mode)
  //sbi(ADCSRA, ADSC);        // ADC start the first conversions
  sbi(ADCSRA, 2);           // 0x111 = clock divided by 128, 125 kHz, 104 us for 13 cycles of one AD conversion, 12 us fo 1.5 cycle for sample-hold
  sbi(ADCSRA, 1);        
  sbi(ADCSRA, 0);        

  pinMode(LED_red, OUTPUT);
  digitalWrite(LED_red, LOW);  
  digitalWrite(RESET, LOW);  
  
  for(int i=0; i<5; i++)  
  {
    delay(50);
    digitalWrite(LED_red, HIGH);  // Blink for Dasa 
    delay(50);
    digitalWrite(LED_red, LOW);  
  }

  // Initiation of RTC
  Wire.beginTransmission(0x51); // init clock
  Wire.write((uint8_t)0x23); // Start register
  Wire.write((uint8_t)0x00); // 0x23
  Wire.write((uint8_t)0x00); // 0x24 Two's complement offset value
  Wire.write((uint8_t)0b00000101); // 0x25 Normal offset correction, disable low-jitter mode, set load caps to 6 pF
  Wire.write((uint8_t)0x00); // 0x26 Battery switch reg, same as after a reset
  Wire.write((uint8_t)0x00); // 0x27 Enable CLK pin, using bits set in reg 0x28
  Wire.write((uint8_t)0x97); // 0x28 stop watch mode, no periodic interrupts, CLK pin off
  Wire.write((uint8_t)0x00); // 0x29
  Wire.write((uint8_t)0x00); // 0x2a
  Wire.endTransmission();
  Wire.beginTransmission(0x51); // reset clock
  Wire.write(0x2f); 
  Wire.write(0x2c);
  Wire.endTransmission();
  Wire.beginTransmission(0x51); // start stop-watch
  Wire.write(0x28); 
  Wire.write(0x97);
  Wire.endTransmission();
  Wire.beginTransmission(0x51); // reset stop-watch
  Wire.write((uint8_t)0x00); // Start register
  Wire.write((uint8_t)0x00); // 0x00
  Wire.write((uint8_t)0x00); // 0x01 
  Wire.write((uint8_t)0x00); // 0x02 
  Wire.write((uint8_t)0x00); // 0x03
  Wire.write((uint8_t)0x00); // 0x04
  Wire.write((uint8_t)0x00); // 0x05
  Wire.endTransmission();
  
  //wdt_reset(); //Reset WDT

  // make a string for device identification output
  String dataString = "$AIRDOS," + FWversion + "," + gittag + ","; // FW version and Git hash

  if (digitalRead(17)) // Protection against sensor mallfunction 
  {
    Wire.beginTransmission(0x58);                   // request SN from EEPROM
    Wire.write((int)0x08); // MSB
    Wire.write((int)0x00); // LSB
    Wire.endTransmission();
    Wire.requestFrom((uint8_t)0x58, (uint8_t)16);    
    for (int8_t reg=0; reg<16; reg++)
    { 
      uint8_t serialbyte = Wire.read(); // receive a byte
      if (serialbyte<0x10) dataString += "0";
      dataString += String(serialbyte,HEX);    
      serialhash += serialbyte;
    }
  }
  else
  {
    dataString += "NaN";    
  }

  Serial.println("#Hmmm...");
  
  {
    set_power(SD_ON);

    delay(100);
    
    // make sure that the default chip select pin is set to output
    // see if the card is present and can be initialized:
    if (!SD.begin(SS)) 
    {
      Serial.println("#Card failed, or not present");
      // don't do anything more:
      return;
    }
  
    // open the file. note that only one file can be open at a time,
    // so you have to close this one before opening another.
    File dataFile = SD.open("datalog.txt", FILE_WRITE);
  
    // if the file is available, write to it:
    if (dataFile) 
    {
      dataFile.println(dataString);  // write to SDcard (800 ms)     
      dataFile.close();
      digitalWrite(LED_red, HIGH);  // Blink for Dasa
      Serial.println(dataString);  // print SN to terminal 
      digitalWrite(LED_red, LOW);          
    }  
    // if the file isn't open, pop up an error:
    else 
    {
      Serial.println("#error opening datalog.txt");
    }
    
    set_power(SD_OFF);
  }    
  
  hits = 0;
  //!!! wdt_reset(); //Reset WDT
}
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

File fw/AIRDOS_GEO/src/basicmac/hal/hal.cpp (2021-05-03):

/*******************************************************************************
 * Copyright (c) 2015 Matthijs Kooijman
 *
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
 * This the HAL to run LMIC on top of the Arduino environment.
 *******************************************************************************/

#define _GNU_SOURCE 1 // For fopencookie
// Must be first, otherwise it might have already been included without _GNU_SOURCE
#include <stdio.h>
#undef _GNU_SOURCE
// Prevent warning on samd where samd21g18a.h from CMSIS defines this
#undef LITTLE_ENDIAN
#include <Arduino.h>
#include <SPI.h>
#include "../basicmac.h"
#include "hal.h"

// Datasheet defins typical times until busy goes low. Most are < 200us,
// except when waking up from sleep, which typically takes 3500us. Since
// we cannot know here if we are in sleep, we'll have to assume we are.
// Since 3500 is typical, not maximum, wait a bit more than that.
static unsigned long MAX_BUSY_TIME = 5000;

// -----------------------------------------------------------------------------
// I/O

static void hal_io_init () {
    uint8_t i;
    // Checks below assume that all special pin values are >= LMIC_UNUSED_PIN, so check that.
    #if defined(BRD_sx1261_radio) || defined(BRD_sx1262_radio)
    LMIC_STATIC_ASSERT(LMIC_UNUSED_PIN < LMIC_CONTROLLED_BY_DIO3, "Unexpected constant values");
    LMIC_STATIC_ASSERT(LMIC_UNUSED_PIN < LMIC_CONTROLLED_BY_DIO2, "Unexpected constant values");
    #endif // defined(BRD_sx1261_radio) || defined(BRD_sx1262_radio)

    ASSERT(lmic_pins.nss < LMIC_UNUSED_PIN);
    ASSERT(lmic_pins.rst <= LMIC_UNUSED_PIN);
    ASSERT(lmic_pins.rx <= LMIC_UNUSED_PIN);

#if defined(BRD_sx1272_radio) || defined(BRD_sx1276_radio)
    //DIO0 is required, DIO1 is required for LoRa, DIO2 for FSK
    ASSERT(lmic_pins.dio[0] < LMIC_UNUSED_PIN);
    ASSERT(lmic_pins.dio[1] < LMIC_UNUSED_PIN || lmic_pins.dio[2] < LMIC_UNUSED_PIN);

    ASSERT(lmic_pins.busy == LMIC_UNUSED_PIN);
    ASSERT(lmic_pins.tcxo == LMIC_UNUSED_PIN);
    ASSERT(lmic_pins.tx <= LMIC_UNUSED_PIN);
#elif defined(BRD_sx1261_radio) || defined(BRD_sx1262_radio)
    // Only DIO1 should be specified
    ASSERT(lmic_pins.dio[0] == LMIC_UNUSED_PIN);
    ASSERT(lmic_pins.dio[1] < LMIC_UNUSED_PIN);
    ASSERT(lmic_pins.dio[2] == LMIC_UNUSED_PIN);

    ASSERT(lmic_pins.busy <= LMIC_UNUSED_PIN);
    ASSERT(lmic_pins.tcxo == LMIC_UNUSED_PIN || lmic_pins.tcxo == LMIC_CONTROLLED_BY_DIO3);
    ASSERT(lmic_pins.tx <= LMIC_UNUSED_PIN || lmic_pins.tx == LMIC_CONTROLLED_BY_DIO2);
#else
    #error "Unknown radio type?"
#endif

    // Write HIGH to deselect (NSS is active low). Do this before
    // setting output, to prevent a moment of OUTPUT LOW on e.g. AVR.
    digitalWrite(lmic_pins.nss, HIGH);
    pinMode(lmic_pins.nss, OUTPUT);
    // Write HIGH again after setting output, for architectures that
    // reset to LOW when setting OUTPUT (e.g. arduino-STM32L4).
    digitalWrite(lmic_pins.nss, HIGH);

    if (lmic_pins.tx < LMIC_UNUSED_PIN)
        pinMode(lmic_pins.tx, OUTPUT);
    if (lmic_pins.rx < LMIC_UNUSED_PIN)
        pinMode(lmic_pins.rx, OUTPUT);
    if (lmic_pins.rst < LMIC_UNUSED_PIN)
        pinMode(lmic_pins.rst, OUTPUT);
    if (lmic_pins.busy < LMIC_UNUSED_PIN)
        pinMode(lmic_pins.busy, INPUT);
    if (lmic_pins.tcxo < LMIC_UNUSED_PIN)
        pinMode(lmic_pins.tcxo, OUTPUT);

    for (i = 0; i < NUM_DIO; ++i) {
        if (lmic_pins.dio[i] < LMIC_UNUSED_PIN)
            pinMode(lmic_pins.dio[i], INPUT);
    }
}

// rx = 0, tx = 1, off = -1
void hal_ant_switch (u1_t val) {
    // TODO: Support separate pin for TX2 (PA_BOOST output)
    if (lmic_pins.tx < LMIC_UNUSED_PIN)
        digitalWrite(lmic_pins.tx, val == HAL_ANTSW_TX || val == HAL_ANTSW_TX2);
    if (lmic_pins.rx < LMIC_UNUSED_PIN)
        digitalWrite(lmic_pins.rx, val == HAL_ANTSW_RX);
}

// set radio RST pin to given value (or keep floating!)
bool hal_pin_rst (u1_t val) {
    if (lmic_pins.rst >= LMIC_UNUSED_PIN)
        return false;

    if(val == 0 || val == 1) { // drive pin
        pinMode(lmic_pins.rst, OUTPUT);
        digitalWrite(lmic_pins.rst, val);
    } else { // keep pin floating
        pinMode(lmic_pins.rst, INPUT);
    }
    return true;
}

void hal_irqmask_set (int /* mask */) {
    // Not implemented
}

static bool dio_states[NUM_DIO] = {0};
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

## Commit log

2021-03-25 solar panel holder
    [SolarHolder.scad]
2021-03-28 temperature graph
2021-04-01 smaller sollar holder
    [SolarHolder.scad, SolarHolder.stl]
2021-04-07 new solar panel holder
    [SolarHolder.scad, SolarHolder.stl]
2021-04-13 initialisation of battery gueage
2021-05-20 old schematics was deleted
    [SIPM01A-B.Cu.gbr, SIPM01A-B.Mask.gbr, SIPM01A-Edge.Cuts.gbr, SIPM01A-F.Cu.gbr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]
2021-06-03 Add g-codes used for printing.
2021-06-08 solar holder with thicker frame
    [SolarHolder.scad, SolarHolder.stl]
2021-06-08 more rugged frame
    [SolarHolder.scad, SolarHolder.stl]
2021-09-01 lorasave.py: Fix it to work with new TTN stack
    After having no luck with making the script as it was work with
    current TTN stack, drop the deprecated ttn library and use a mqtt client
    library directly. Now it picks up messages.
2021-09-19 Solar Holder for bigger solar panel
    [SolarHolder_big.scad]
2021-09-20 Solar Holder -- optimization, cleaner code, fixed warning
    [SolarHolder_big.scad]
2021-09-26 Added "triangles" and nut sizes
    [SolarHolder_big.scad]
2021-09-26 Added second screw
    [SolarHolder_big.scad]
2021-09-26 Fixed fn
    [SolarHolder_big.scad]
2021-09-26 Moved the screw for the panel
    [SolarHolder_big.scad]
2021-09-26 cleaner code
    [SolarHolder_big.scad]
2021-09-26 Render new holder model.
    [SolarHolder_big.amf, SolarHolder_big.stl]
2021-09-26 Model prepared for printing. #3
2021-10-18 Improve sensor documentation.
2021-12-19 drzak na valcovy krystal
    [NaITl_big.scad, configuration.scad]
2021-12-21 box holder
    [BoxHolder.scad]
2021-12-22 GPS permanent power on
2021-12-26 Stolek pro Spacedos
    [SpacedosHolder.scad]
2021-12-29 Improve documentation of programming cable connection.
2022-01-15 antenna holder
    [antenna_holder.scad]
2022-10-05 reset hits even sensor malfunction

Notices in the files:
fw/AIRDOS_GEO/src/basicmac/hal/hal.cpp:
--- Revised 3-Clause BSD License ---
